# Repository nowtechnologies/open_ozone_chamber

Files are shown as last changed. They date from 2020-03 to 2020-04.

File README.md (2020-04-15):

# SMOG-SC / O3 Sterilizer

*Scalable Modular Ozone Generation based Sterilization Chamber ( SMOG-SC )*

This project aims to lay down general design instructions for an ozone generation based sterilization chamber that could be deployed fast to medical environments. The design is layered and modular to take component availability into account.

## About ozone

Ozone (O3) is an unstable gas comprising three atoms of oxygen. It is unstable because the gas will readily degrade back to its stable state, diatomic oxygen (O2) with the formation of free oxygen atoms or free radicals. The free oxygen atoms or radicals are highly reactive and they will oxidize almost anything  including viruses, bacteria, organic and inorganic compounds) in contacts, making ozone an enormously powerful disinfectant and oxidizer. 

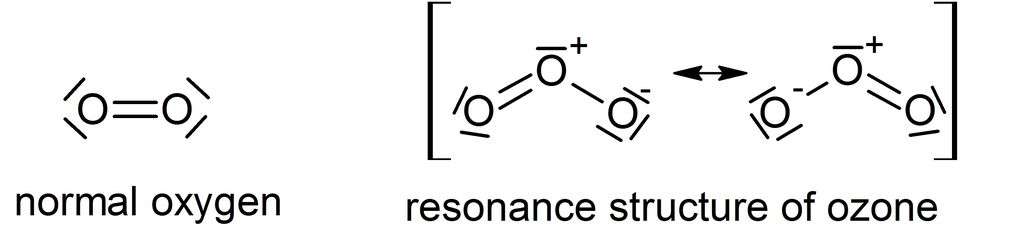
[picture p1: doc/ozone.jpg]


:warning: **Ozone with concentration higher than 1 ppm has adverse effects on human health and the use of ozone for air disinfection is generally not recommended if people are around.** :warning:

The MAC-value is the Maximum Acceptable Concentration a human is allowed to be exposed to for a certain time and certain agent. For ozone the MAC-values is **0.06 PPM for 8 hours a day, 5 days a week** (PPM = Parts Per Million). For a maximum of 15 minutes a MAC-value of 0.3 PPM is applied.

Read more: https://www.lenntech.com/library/ozone/decomposition/ozone-decomposition.htm

| **Temp (°C)** | Half live   |
| ------------- | ----------- |
| -50           | 3 months    |
| -35           | 18 days     |
| -25           | 8 days      |
| 20            | 3 days      |
| 120           | 1,5 hours   |
| 250           | 1,5 seconds |

**Dissolved in water (pH 7)**

| **Temp (°C)** | **Half** **live** |
| ------------- | ----------------- |
| 15            | 30 min            |
| 20            | 20 min            |
| 25            | 15 min            |
| 30            | 12 min            |
| 35            | 8 min             |

* Ozone breaks down to oxygen with a half life of about 20 minutes ( at 20 degrees Celsius in water )
* Decomposition of 2 mol (96 g) ozone to 3 mols of oxygen requires 286 kJ energy
* pH influences acid/base equilibriums of some compounds and also the reaction speed of ozone.
* Decay of ozone in a basic environment is much faster than in an acid environment!
* [Materials ozone resistance chart](https://www.oxidationtech.com/blog/materials-ozone-resistance-chart/)
* [Ozone decomposition kinetics](doc/Ozone_decomposition_kinetics.pdf)

## Decontamination protocol

The standard program adopted involves increasing the ozone level over a period of 15 min to 25 ppm, maintaining this level for 10 min, at which point the humidifier was activated to produce a rapid burst of water vapor. This should result in the RH increasing to > 95% within 5 min. Following this the humidifier and generator are switched off and the catalytic converter is switched on, which results in decrease in ozone to < 1 ppm within 15 min. [Hudson et al.](doc/Ozone_Science_and_Engineering_Pub_Jan091.pdf)

## Device requirements

* Hermetically sealed sterilization chamber *( when door is closed )*
* Effective minimum concentration of ozone is 25 ppm **~50 mg/m3** *( 1 ppm (O3) = 2.14 mg/m3 )*
* To meet protocol parameters **for every cubic meter** a generator capacity of **~200 mg/h** is required.
* Air humidity shall be controlled so that RH could be increased to **> 95%** rapidly. *( optional )*
* There should be a **timed lock**, to prevent the user to open the device while operating. *( optional )*
* There should be a clear **sign** indicating potentially dangerous oxidant levels inside the device.
* Ozone **levels** should be either measured or predicted by its decomposition model.
* Temperature and humidity can be easily monitored. *( supporting the level prediction - optional )*

## System block diagram

:warning: **Note**: our open design is only recommended in emergency situations, where sufficient ventilation of the room can be provided!

The system can be either completely closed or partially open, where the ionized air can travel through the chamber into a catalyst. For the sake of simplicity we chose the closed system design with the <u>generator and the decomposer inside the sterilization chamber</u>.

Either way the sterilizer system consists of four separate modules that can be <u>bought or built</u>:

* The **generator** is turning atmospheric oxygen into ozone enriched air.
* The ozone enriched air is pumped into a sealed **chamber**. 
* The **decomposer** that helps to break down ozone to oxygen.
* The **controller** is regulating the sterilization process.

#### Open system

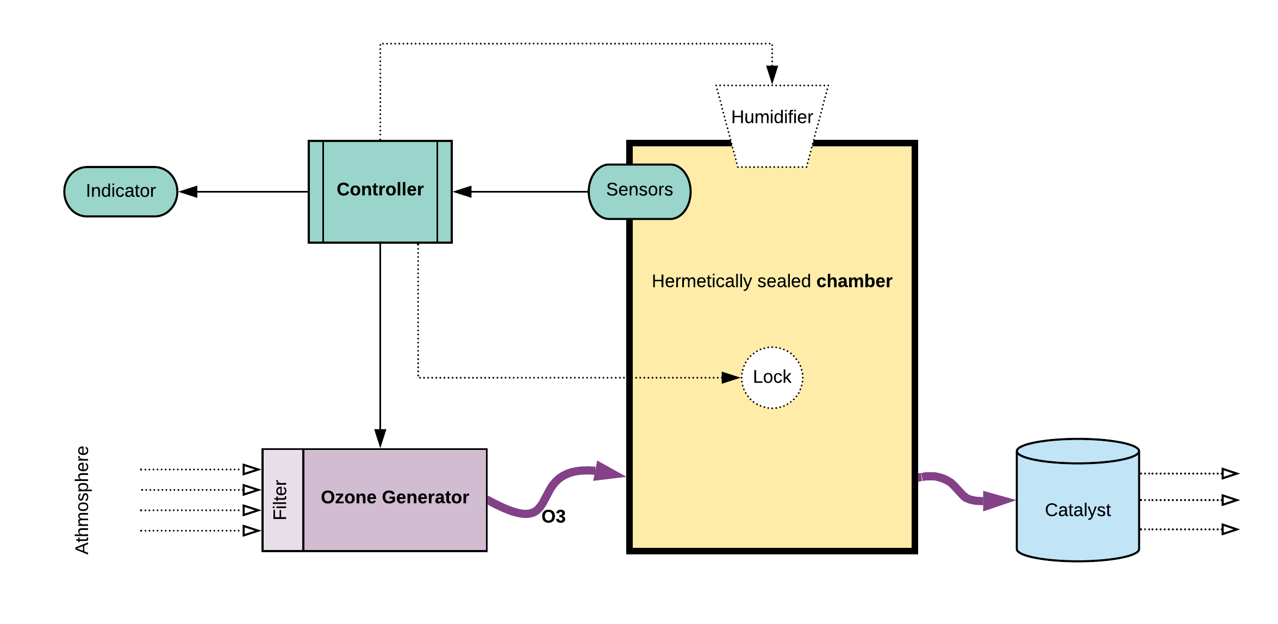
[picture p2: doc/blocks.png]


#### Closed system

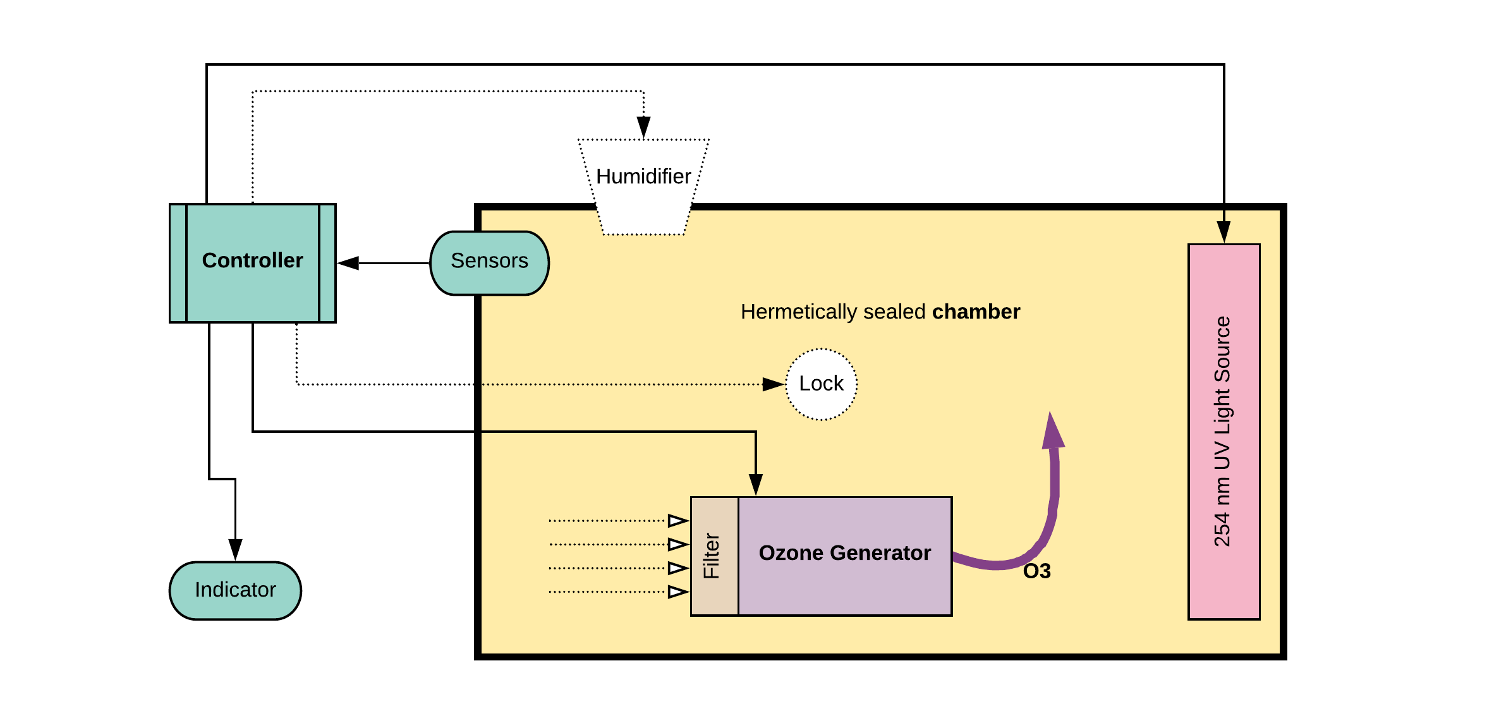
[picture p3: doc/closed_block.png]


### [Ozone generator](doc/ozone_generator.md)

A coronal discharge method based generator consists of:

* HEPA filter on the atmospheric air intake port *( optional )*
* A fan or blower that moves the air volume along the electrodes. *( AC or low voltage DC )*
* The electrodes or *"ozone plates"* provide surface for the corona discharge. *( ceramic )*
* A high voltage power supply ( output **~3.5kV / 30mA** ) is required to drive the plates.
* Exhaust port to channel the O3 enriched air into an ozone resistant tube.

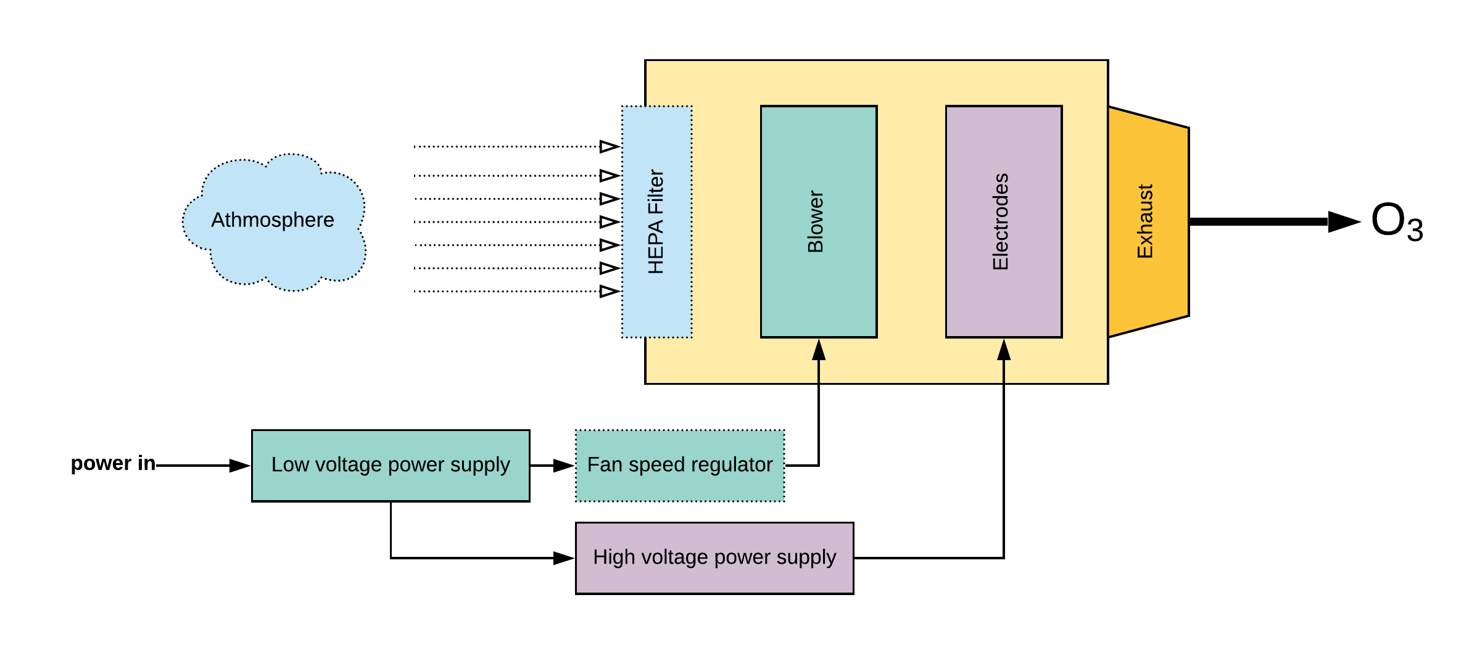
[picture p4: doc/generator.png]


For ultraviolet radiation based ozone production: *( this method is less efficient )*

* Powerful light emitter with a spectral peak of 185 nm.
* A fan or blower that moves the air.

### [Sterilization chamber](doc/steril_chamber.md)

* The chamber has to be somewhat airtight as the ozone is harmful to humans as well.
* Ozone, temperature and humidity sensors has to be placed inside.
* Ideally an electric lock should block the door.

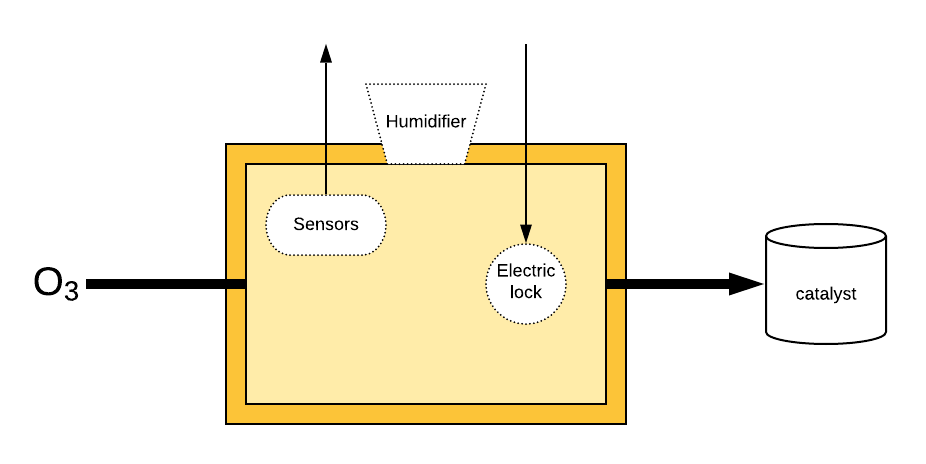
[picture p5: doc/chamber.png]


### [Decomposer](doc/decomposer.md)

Ozone can be reduced to oxygen **thermally** or **catalytically** or **by radiation**. 

*In case of a closed system:*

* The chamber has to hold light sources at **254 nm** wavelength with sufficient power to disrupt the instable bonds in ozone molecules.

*In case of an open system:*

* The ozone enriched air from the chamber has to be able to enter the decomposer.
* In case of catalytic destruction the decomposer could be a bucket of tap water.
* If the pH can be controlled, basic environment is preferable. *( Pka  = 10,3 )*
* Thermal decomposition is effective if the air flows through a tube heated to **250 C** *( HL = 1.5s )*

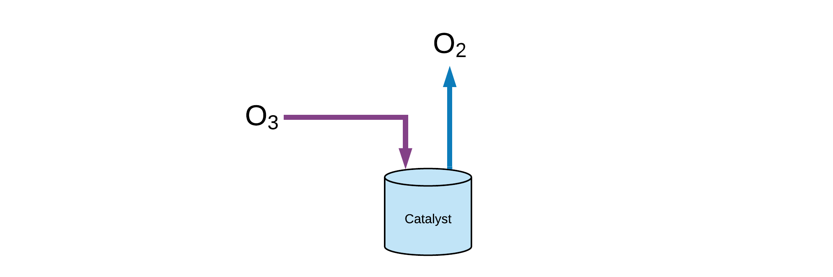
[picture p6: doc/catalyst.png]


### [Process controller](doc/ots_controller.md)

*  There are ready made [ozone controllers](http://www.iaq.hu/F2077TSM-O3%20ozontavado.pdf) with relayed outputs.

**Otherwise a controller could consist of:**

*  MCU chip or board *( general programmable micro controller board e.g. Nucleo or Arduino )*
* Temperature sensor to support the decomposition model and compensate for ozone readings.
* Humidity sensor to check protocol requirements are met and compensate for ozone readings.
* Ozone sensor as control feedback and to check protocol requirements.
* Optional user interface *( Small OLED display and rotary encoder )* for setting chamber parameters
* Single button to start / stop sterilization process.
* Process indicator *( e.g. large LED )*
* Interfaces to control the ozone generator, humidifier and lock. *( e.g. solid state relays )*

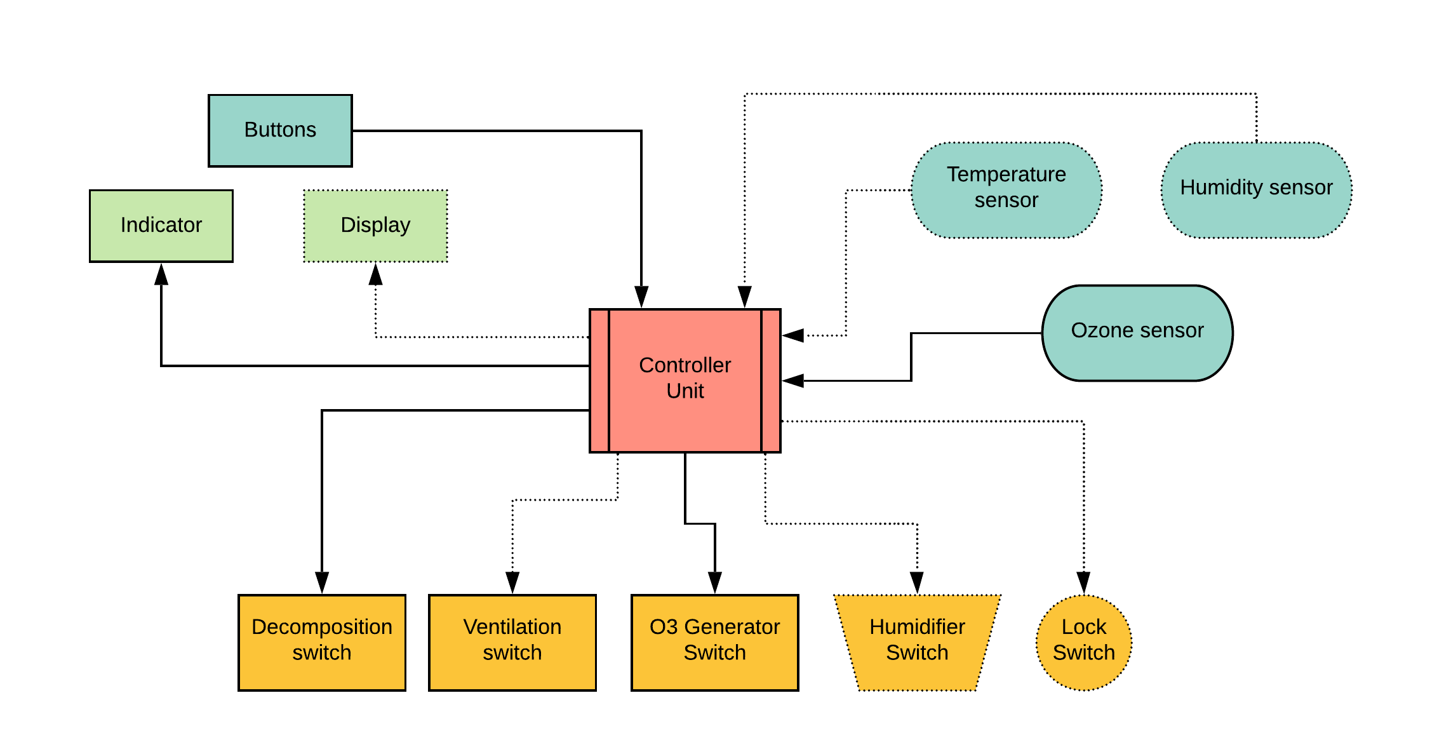
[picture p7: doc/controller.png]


## Build instructions

### Closed system assembly

1. [Modify a refrigerator](doc/refrigerator.md)
2. [Buy an off the shelf generator module](doc/ozone_generator.md)
3. [Buy an off the shelf ozone controller](doc/ots_controller.md)

### How to build an Ozone Generator

* If an off-the-shelf generator is not available:
  * Here is how to [build it from modules](doc/ozone_generator.md). 
  * And if you can't find modules anymore here is how to [build it from components](doc/ozone_generator.md).
* Find information on [how to create the electrodes](doc/electrodes.md) itself.
* Generator [capacity measurement instructions](doc/capacity.md).

### How to build and Ozone Sensor

[Open ozone sensor](https://github.com/nowtechnologies/open_ozone_sensor)

### How to build and Ozone Monitor

[Open ozone monitor](https://github.com/nowtechnologies/open_ozone_monitor)

### How to build an Ozone Controller

[Open ozone controller](https://github.com/nowtechnologies/open_ozone_controller)

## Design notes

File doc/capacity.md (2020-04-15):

# Determining generator capacity

For detailed description of different methodologies please read the article of *Kerwin Rakness* on **Guideline for Measurement of Ozone Concentration in the Process Gas From an Ozone Generator** [here](Ozone_measurement.pdf).

Follow [Oxidation Technologies Measurement protocol](https://www.oxidationtech.com/ozone/ozone-production/how-to-test-production-from-your-ozone-generator/test-o3-output-commercial.html):

An **ozone meter** will be required to measure ozone concentration in the air leaving the ozone generator. This must have a sample pump to draw a sample of gas from your flow tube into the monitoring device. This will provide the most accurate ozone measurements without disrupting your air flow. Ideally a UV based ozone analzyer will be used to measure ozone levels due the greater precision and accuracy available. However, there are some ozone meters available using electrochemical or HMOS sensor cells that can pull a gas sample into the sensor and provide reasonable accuracy. For the best accuracy in ozone production choose the most accurate ozone meter possible.

The specific ozone analyzer we recommend to use for this testing is the [UV-100 Ozone Analyzer.](https://www.oxidationtech.com/products/ozone-monitors/uv-analyzer/uv100-ozone-analyzer.html) This is available[ for sale](https://www.oxidationtech.com/products/ozone-monitors/uv-analyzer/uv100-ozone-analyzer.html), or [for rent for shorter term needs.](https://www.oxidationtech.com/products/rent-ozone/uv-100-rental.html)

A **Monometer** is used to measure airflow by measuring the velocity of airflow in your flow tube. A digital monometer can be obtained that will measure airflow in a variety of units of measure. For the best accuracy in ozone production choose the most accurate monometer possible.

A **Flow Tube** must be constructed to measure airflow from the ozone generator. This tube can be constructed of PVC or other plastic materials. The airflow from the ozone generator must have as much turbulence removed as possible to accurately measure air speed. This tube must be sealed directly to the outlet of the ozone generator and must not restrict air flow in any way. Actual air flow of the ozone generator in normal operation must be obtained and measured accurately.

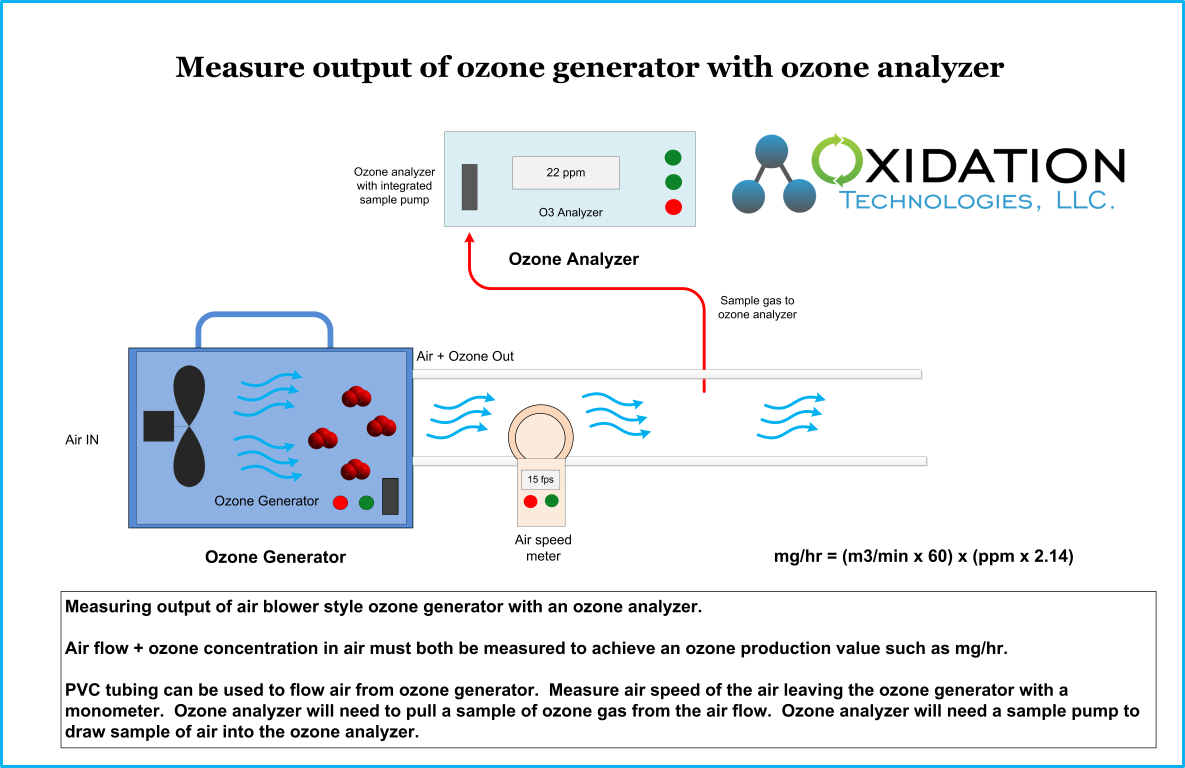
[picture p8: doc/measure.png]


## Ozone meters

Simplest way to determine the capacity of a generator is with a calibrated measurement unit, such as this:

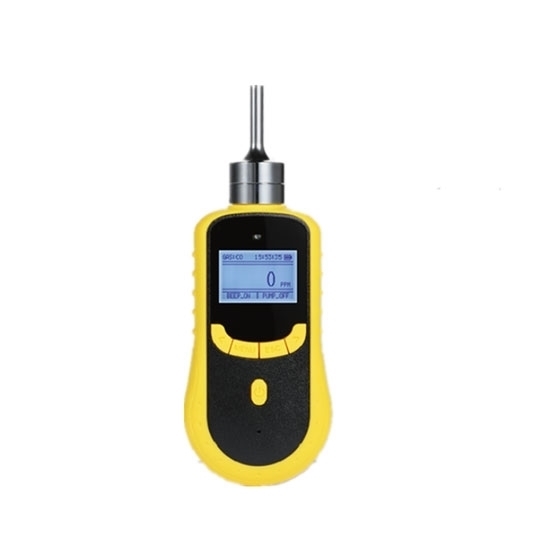
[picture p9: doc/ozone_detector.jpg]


* Typical range 10 ppm - 1000 ppm
* Price 250 - 1500 EUR

## Open ozone sensor + PC GUI

#### [OO/Sensor](https://github.com/nowtechnologies/open_ozone_sensor)

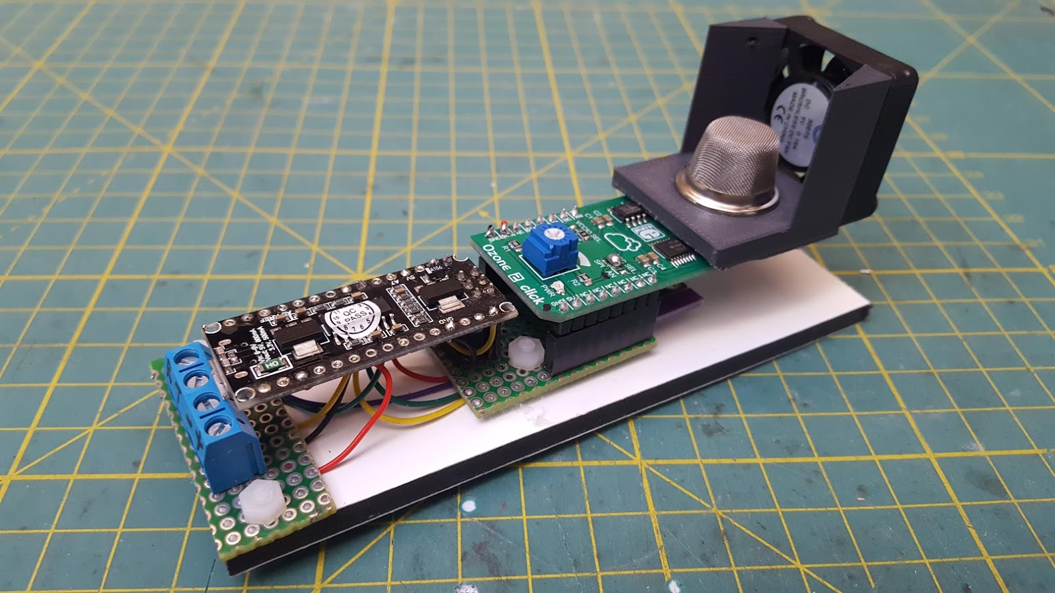
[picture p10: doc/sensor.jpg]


* Typical range 10 ppm - 1000 ppm
* Price <50 EUR

#### [OO/Monitor](https://github.com/nowtechnologies/open_ozone_monitor)

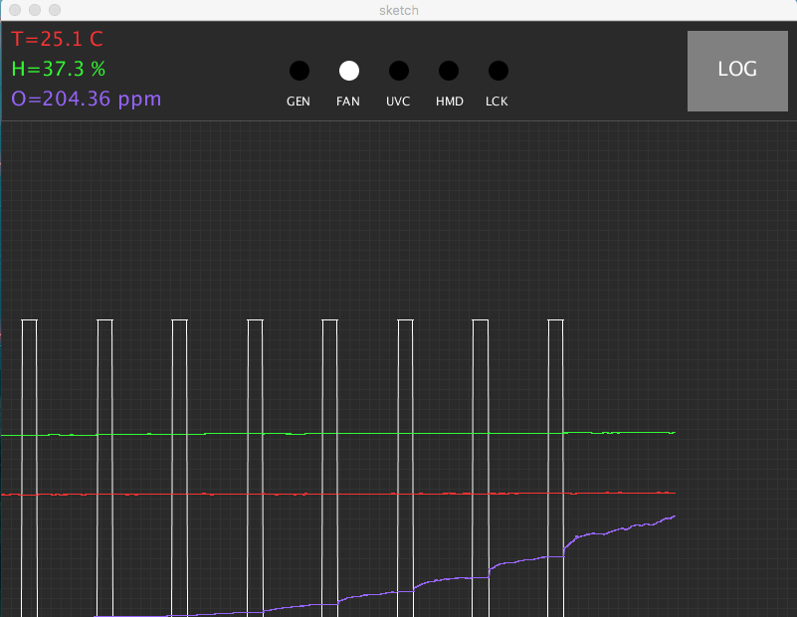
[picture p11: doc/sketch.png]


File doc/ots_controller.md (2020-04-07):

# Process controller

## Ozone controllers

https://www.ecosensors.com/product/os-6-ozone-controller-data-sheet/

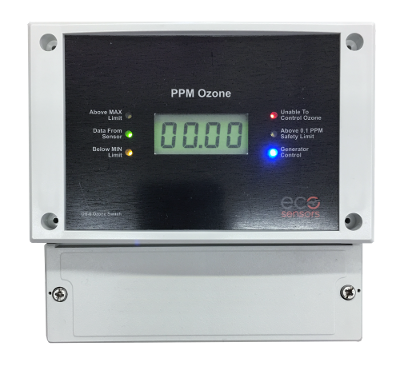
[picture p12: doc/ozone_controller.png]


The OS-6 is an industrial grade ozone controller and monitor. The OS-6 design has been optimized for accuracy, ease of installation, setup and operation. The OS-6 is only available with the SM-7/SM-EC in two different concentration ranges.

**Features:**

- Industrial strength, water resistant enclosure.
- Large digital display, auto-ranging (0-50ppm) w/ backlight.
- Easy front panel access to set points and relays.
- Precisely adjustable max, min, and fail time set points.
- Failure alarm if ozone remains outside control range.
- Front panel generator control cutoff switch for easy maintenance.
- User selectable PPM ranges for analog output (4-20 mA and 0-2 VDC)
- OSHA 0.1 ppm safety limit light.

## Open Ozone Controller

[Github project](https://https://github.com/nowtechnologies/open_ozone_controller)

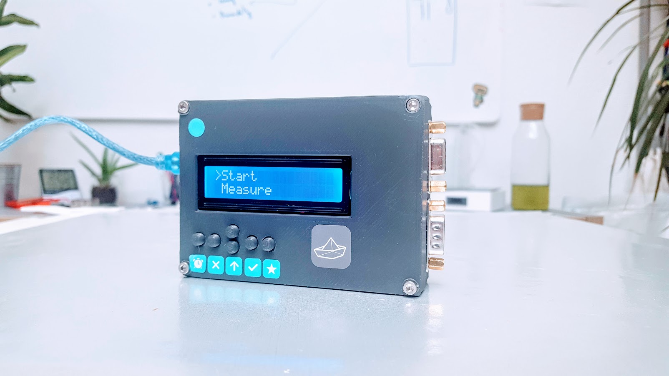
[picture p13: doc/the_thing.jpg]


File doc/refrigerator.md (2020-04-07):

# D.I.Y. sterilization chamber 

*How to modify a refrigerator*

## Tools

* Side cutter
* Screw driver
* Knife
* Duct tape

## Preparing the refrigerator 

Refrigerators seal very good in general hence they are good candidates as a sterilization chamber. They are fairly easy to acquire as every household has one, but it can be utilized **only after a careful preparation** as in many cases it contains **flammable gas!** 

:warning:**Please follow [this link](https://www.kth.se/en/2.2145/energiteknik/forskningsavdelningar/ett/projekt/koldmedier-med-lag-gwp/low-gwp-news/nagot-om-koldmediers-brannbarhet-1.575938) to learn more about the refrigerant in your device before proceeding.** :warning:

### Remove the electric plug

Find the distributor box ( probably near the compressor ), pull the cables out so that you can see their color codes ( if possible ) then cut them one by one. Don't throw out the cable with the wall plug, we are going to reuse it.

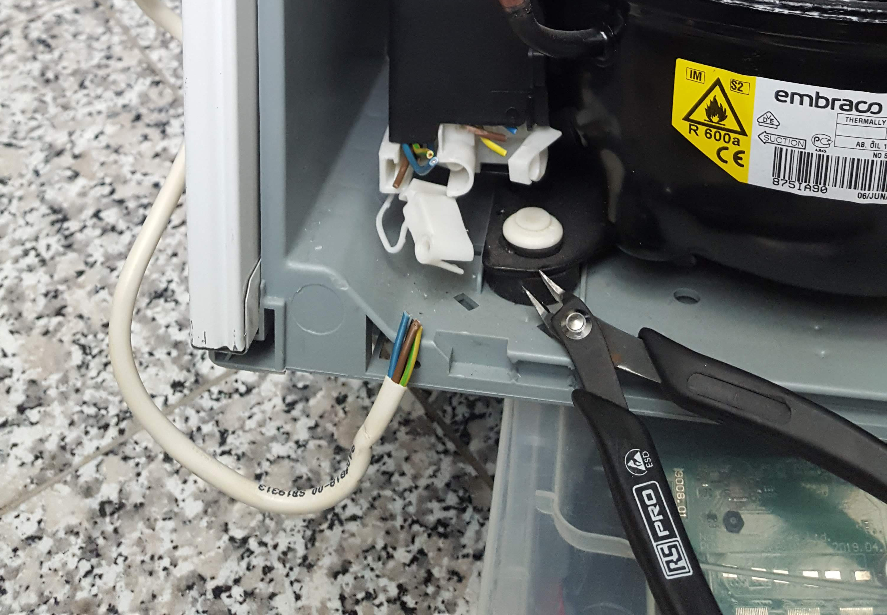
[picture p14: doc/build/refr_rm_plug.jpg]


### Degassing :warning:

This step is **dangerous** as most refrigerators in Europe are filled with **R600** gas that is highly flammable. The system has to be degassed very slowly to avoid risk. Take the refrigerator outside to **open air** before continuing with this step! **Avoid any probability and proximity to open flame or sparks at all times during the degassing process.**

1. Find a cartridge shaped gas puffer that has - usually - a thinner copper tube coiled around it.
2. **Cut the thin copper tube and step aside until you don't hear it hiss anymore.** *( marked as 1st )*
3. Now cut the thicker copper tube connected to the cartridge *( marked as 2nd )*
4. After this you can cut any other copper tubing wherever you want.

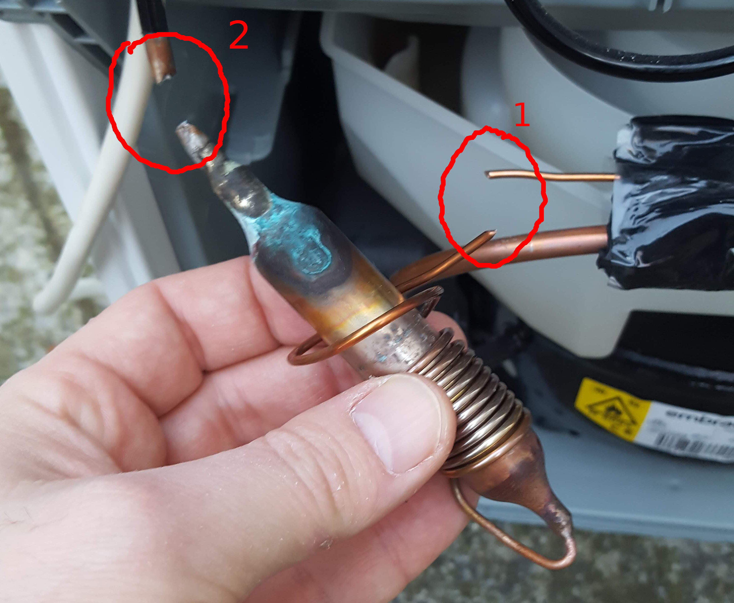
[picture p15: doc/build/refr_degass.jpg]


### Remove the cooler plate

Cut the remaining tubing that connects the cooler plate. Remove the screws or patents that hold the cooler on it's place and get rid of the plate.

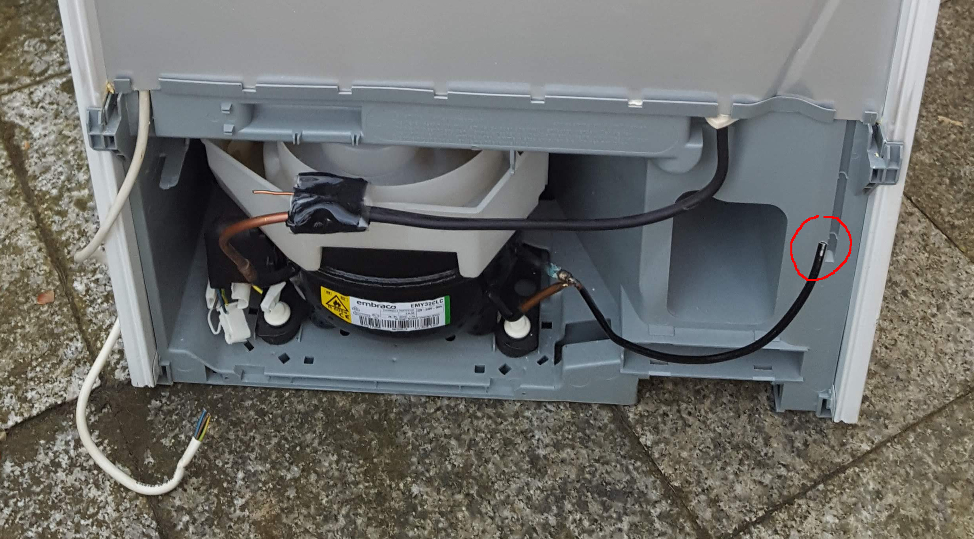
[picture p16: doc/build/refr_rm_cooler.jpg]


### Remove the compressor

Now that the cooler plate gone, cut the last copper tube that connects the compressor. Remove screws or patents holding it in it's place, then remove the compressor.

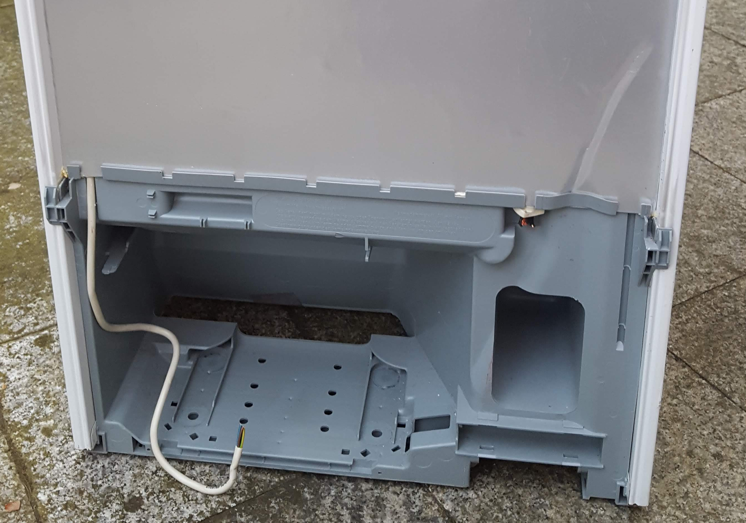
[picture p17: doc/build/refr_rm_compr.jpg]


### Seal the sinker hole

Every refrigerator has a hole to allow the damp to drip down. **This has to be sealed!** Use silicone or duct tape to seal it.

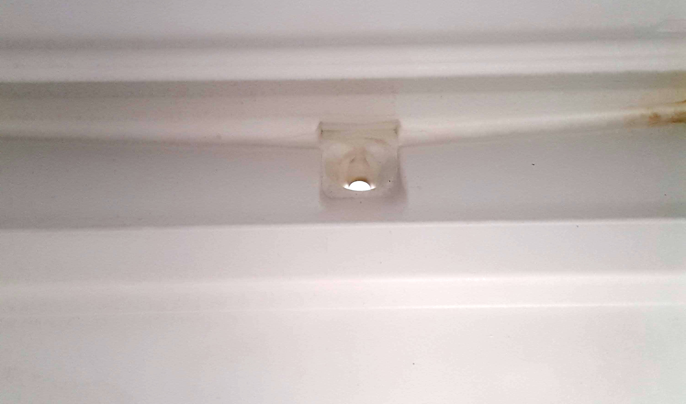
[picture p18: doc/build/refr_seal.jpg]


### Remove the switch and light

There is usually a switch and a light bulb inside the icebox that leaves us an opportunity to use it's wiring to power the ozone generator without drilling a hole into the fridge. *( The switch could be used to disable the generator when the door has been opened, so don't throw it away. )* Remove the whole pack.

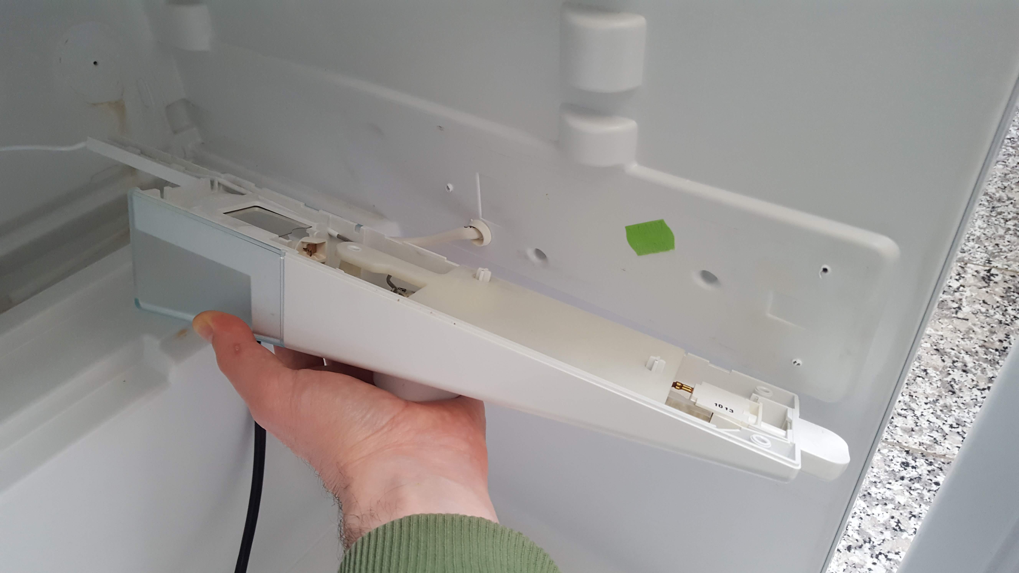
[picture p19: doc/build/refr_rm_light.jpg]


## Rewiring

### Prepare the wall plug

Use screw terminal block to connect the three wires of the wall plug cable to the three wires of the light cable, maintain color coding. The ozone generator requires a properly grounded connection.

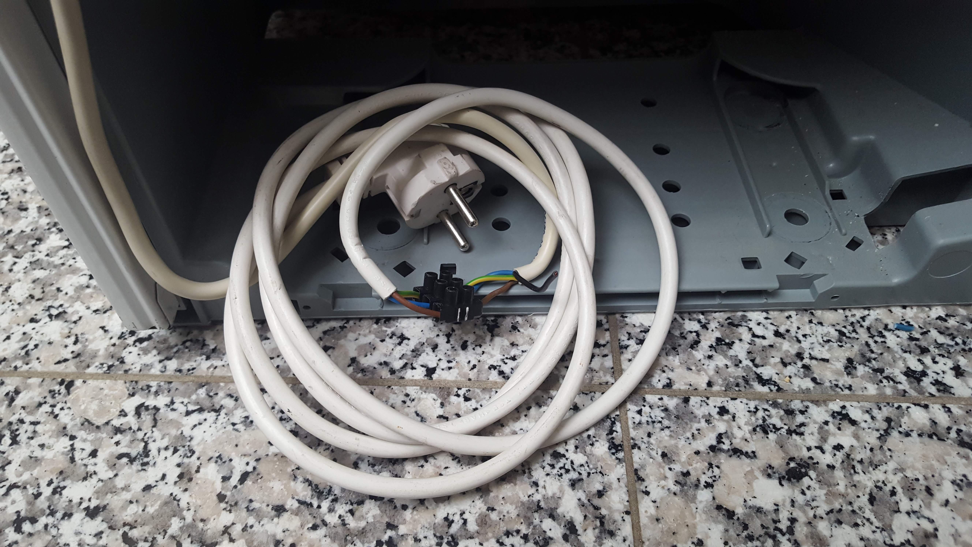
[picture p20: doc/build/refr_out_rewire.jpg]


### Add internal terminals

Now add screw terminals to the internal end of the same cable. *( Note: there is sometimes an extra black wire for the switch, just ignore it for now. )*

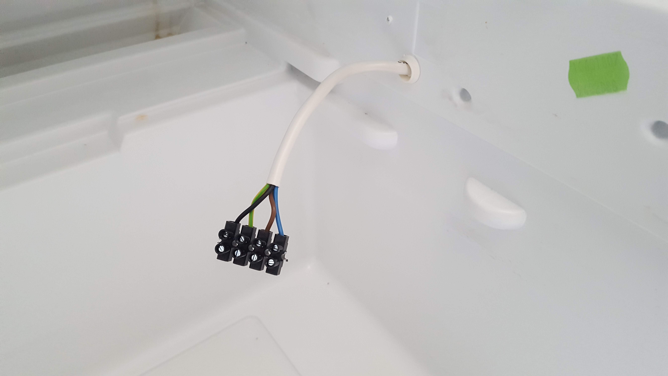
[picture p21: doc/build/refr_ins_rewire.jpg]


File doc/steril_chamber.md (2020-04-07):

# Sterilization chamber



## Off the shelf cabinets

**Requirements:**

* Preferably stainless steel
* Hermetically seal-able

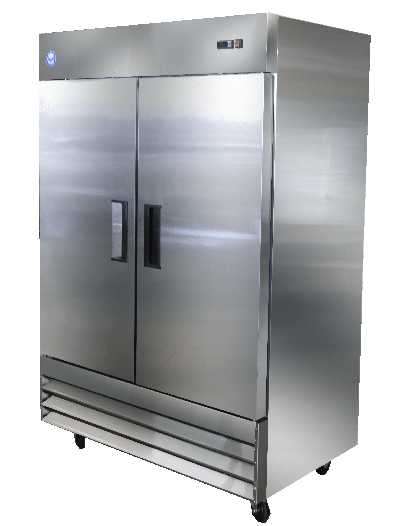
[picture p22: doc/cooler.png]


## Refrigerators

Refrigerators seal very good in general hence they are good candidates as a sterilization chamber. They are fairly easy to acquire as every household has one, but it can be utilized **only after a careful preparation** as in many cases it contains **flammable gas!** 

[Here is how to modify one.](refrigerator.md)

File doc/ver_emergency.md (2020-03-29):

# How to build a sterilizer blazing fast

:warning: These instructions are for emergency situations, where all off-the-shelf components are at hand and there is very short time to produce a working sterilizer. In any other case please build one that has an ozone detector based process controller.

### :construction: WARNING: Disinfection protocols are not finalized yet! :construction:

## Components

* Refrigerator
* Ozone generator
* Timer switch
* Screw terminal block

## Tools

* Side cutter
* Screw driver
* Knife
* Duct tape

## Preparing the refrigerator 

Refrigerators seal very good in general hence they are good candidates as a sterilization chamber. They are fairly easy to acquire as every household has one, but it can be utilized **only after a careful preparation** as in many cases it contains **flammable gas!** 

:warning:**Please follow [this link](https://www.kth.se/en/2.2145/energiteknik/forskningsavdelningar/ett/projekt/koldmedier-med-lag-gwp/low-gwp-news/nagot-om-koldmediers-brannbarhet-1.575938) to learn more about the refrigerant in your device before proceeding.** :warning:

### Remove the electric plug

Find the distributor box ( probably near the compressor ), pull the cables out so that you can see their color codes ( if possible ) then cut them one by one. Don't throw out the cable with the wall plug, we are going to reuse it.



### Degassing :warning:

This step is **dangerous** as most refrigerators in Europe are filled with **R600** gas that is highly flammable. The system has to be degassed very slowly to avoid risk. Take the refrigerator outside to **open air** before continuing with this step! **Avoid any probability and proximity to open flame or sparks at all times during the degassing process.**

1. Find a cartridge shaped gas puffer that has - usually - a thinner copper tube coiled around it.
2. **Cut the thin copper tube and step aside until you don't hear it hiss anymore.** *( marked as 1st )*
3. Now cut the thicker copper tube connected to the cartridge *( marked as 2nd )*
4. After this you can cut any other copper tubing wherever you want.



### Remove the cooler plate

Cut the remaining tubing that connects the cooler plate. Remove the screws or patents that hold the cooler on it's place and get rid of the plate.



### Remove the compressor

Now that the cooler plate gone, cut the last copper tube that connects the compressor. Remove screws or patents holding it in it's place, then remove the compressor.



### Remove the switch and light

There is usually a switch and a light bulb inside the icebox that leaves us an opportunity to use it's wiring to power the ozone generator without drilling a hole into the fridge. *( The switch could be used to disable the generator when the door has been opened, so don't throw it away. )* Remove the whole pack.



## Rewiring

### Prepare the wall plug

Use screw terminal block to connect the three wires of the wall plug cable to the three wires of the light cable, maintain color coding. The ozone generator requires a properly grounded connection.



### Add internal terminals

Now add screw terminals to the internal end of the same cable. *( Note: there is sometimes an extra black wire for the switch, just ignore it for now. )*



### Prepare generator cable

Now repeat the step with the cable provided for the generator, and connect it to the terminals inside the fridge. Make sure it's long enough to place the generator anywhere you planned.

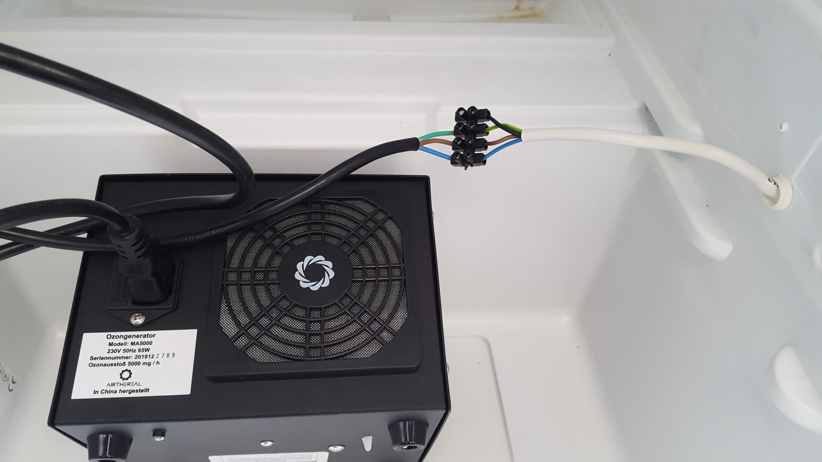
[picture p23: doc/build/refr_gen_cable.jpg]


### Install the generator

Place the generator so that neither the intake for it's fan nor the exhaust panel is blocked. 

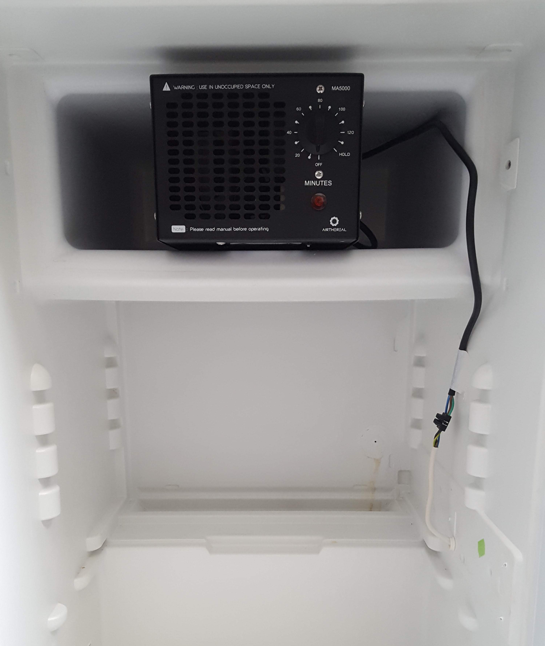
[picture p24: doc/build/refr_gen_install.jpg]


### Seal the sinker hole

Every refrigerator has a hole to allow the damp to drip down. **This has to be sealed!** Use silicone or duct tape to seal it.



## Using the emergency sterilizer

:warning: Please use this device only if you are sure that you can vent the room frequently, as without precise controller there is going to be excess ozone gas in the container on the end of each sterilization cycle. Follow procedure and do not exceed MAC exposure. **MAC = 0.06 PPM for 8 hours a day, 5 days a week.**

### Enable continuous generator operation

Most generators' - that have analogue timer built in - continuous operation can be enabled, by selecting the "hold" function on their dial. If you are using a more precise timer, or an ozone controller you should enable this function on the generator. ( If there is no such dial, then the device is probably already in continuous operation mode. If there is no "hold" function on the dial, the device has to be disassembled and the timer switch has to be shorted. )

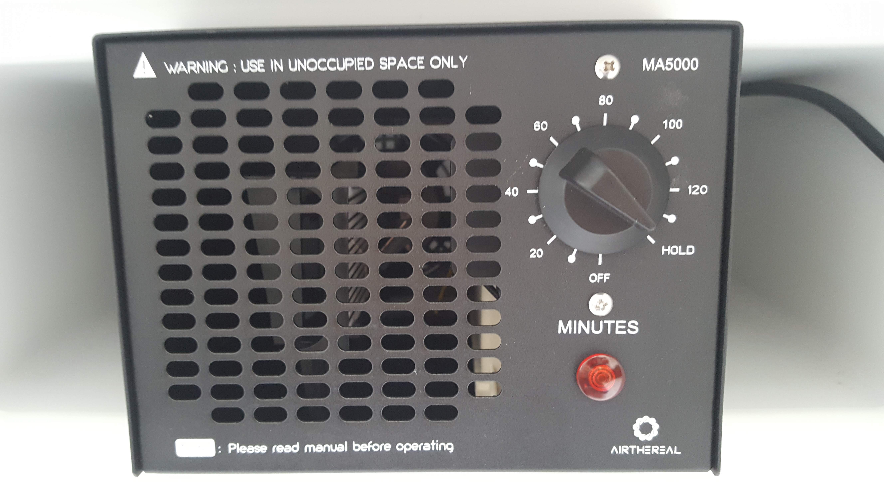
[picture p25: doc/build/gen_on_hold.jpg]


### Preparations

:warning: **Use our [volume to treatment time converter tool](http://nowtech.cloud/closed_calc.html) to figure out the timing protocol.** For smaller containers and large generators meant for room sized air purification the treatment times are going to be under a minute.

:warning: Most timer switches embedded into the generators are not able to do sub-minute timing. **You have to connect the system through a digital or analogue timer switch that is able to do the precise time switching.**

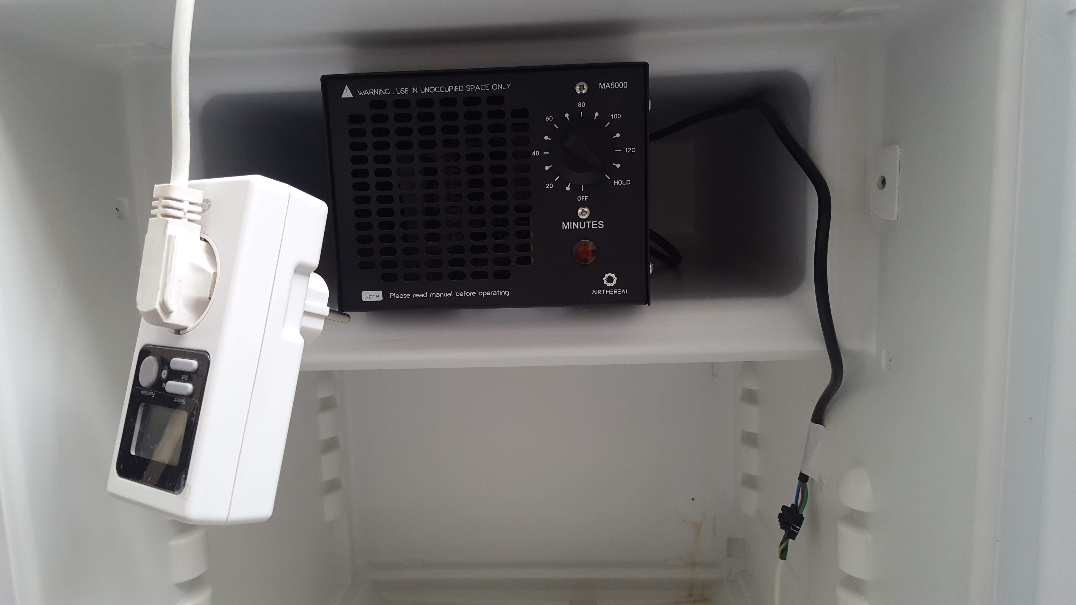
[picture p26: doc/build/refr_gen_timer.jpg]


# :construction:

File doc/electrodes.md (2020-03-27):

# Electrode alternatives

## Glass tube

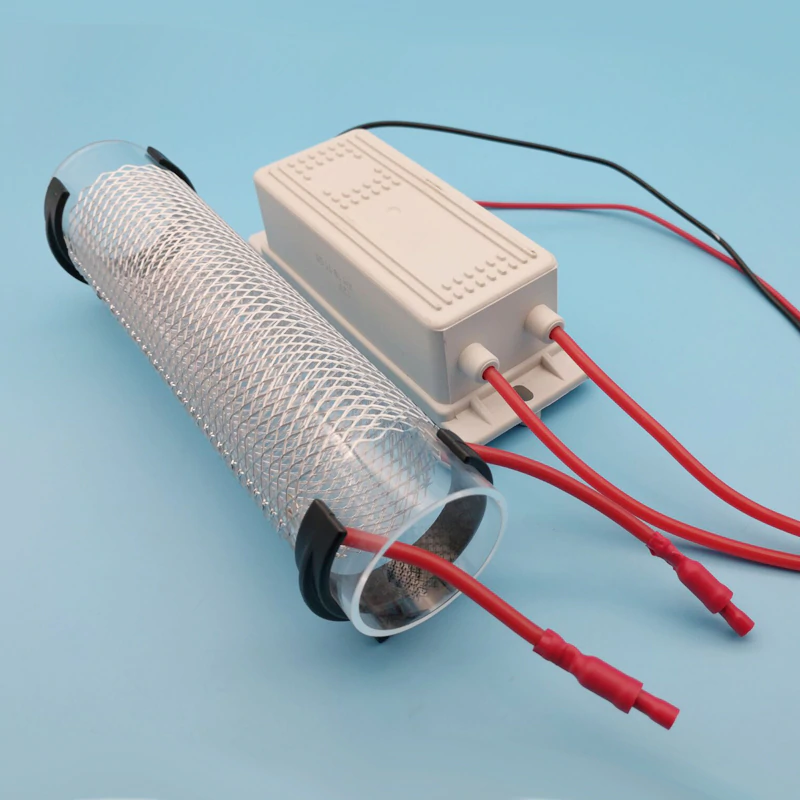
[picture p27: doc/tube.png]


## Stainless steel saw

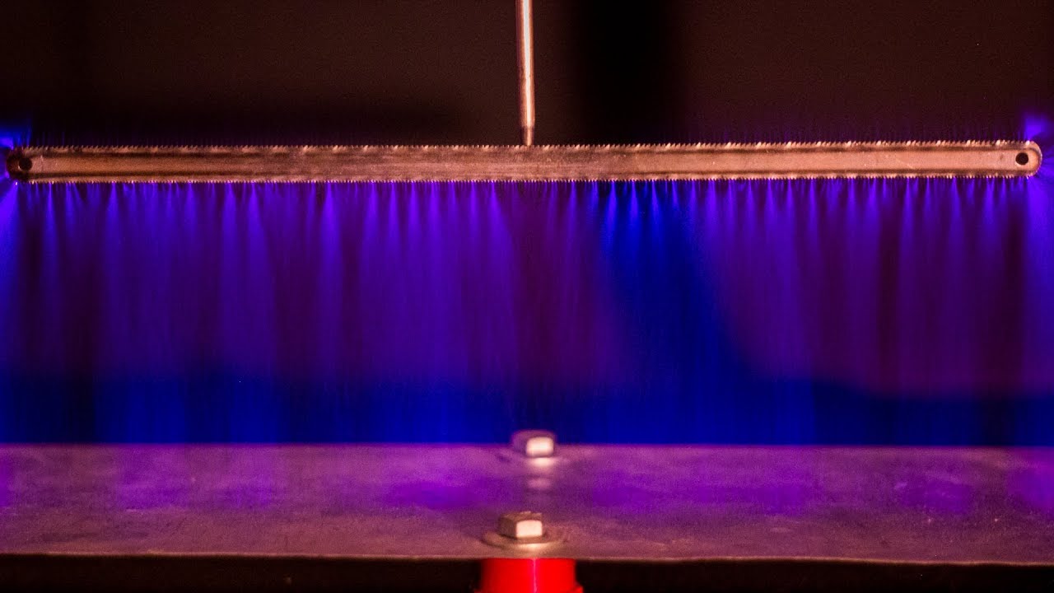
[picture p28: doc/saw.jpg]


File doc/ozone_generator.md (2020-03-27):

# Ozone generator



## Off the shelf generators

Room and car air purifiers can meet the requirements if we take into consideration that **for every cubic meter** a generator capacity of **~200 mg/h** is required. Mid-sized generators for homes produce between 2.5 - 10 grams / hour.

#### Advantages

* Fastest way to start with. *( Put it in a closed chamber and turn it on for n minutes. )*
* It has been built and tested.
* It has the capacity to sterilize a complete room. *( 5-10 g/h )*
* The indicator and timer is already built in. *( also potential disadvantage )* 

#### Disadvantages

* Price range can vary from 100-1000 EUR.
* It runs only from AC. *( battery operation requires disassembly or an inverter )*
* There might be some difficulties with the supply chain.

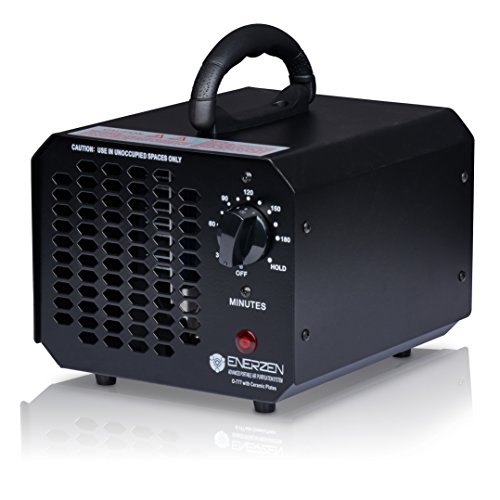
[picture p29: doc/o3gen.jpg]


## Ozone generator modules

Generator modules come in different shapes and sizes, the most frequent types are based on ceramic plate electrodes. These modules also easily met the minimum capacity requirements. As a thumb rule one plate *( ~100x50mm )* can produce ~5 g/h ozone. The modules can be either DC or AC powered by type.

#### Advantages

* Fairly fast way to start with.
* Functional module, already tested.
* More then enough capacity.
* Easy to scale up.
* Easy to control.
* Fair price *( as of know ~30 EUR for a 10 g/h module )*

#### Disadvantages

* All the other components needs to be built around it. 
* There might be some difficulties with the supply chain. *( as produced in China )*

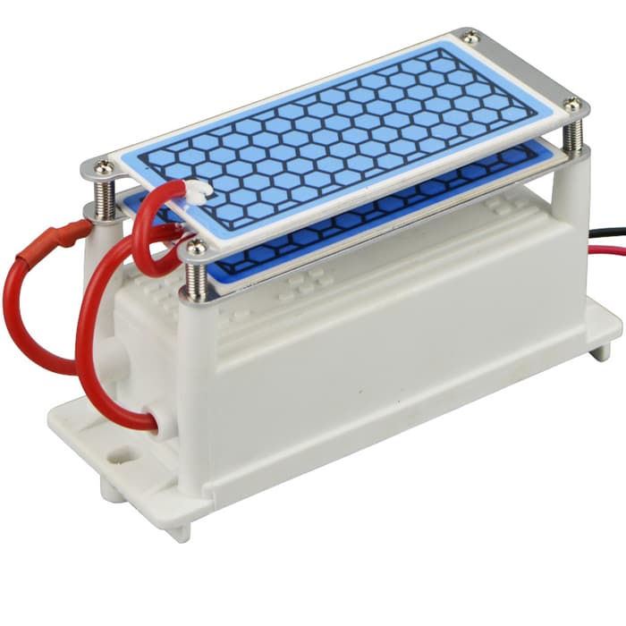
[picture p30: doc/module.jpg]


#### Simple generator configuration

The most easy to assemble setup for a functional generator is to an AC fan ( ~100 CFM = ~170 m3/h ) with an AC generator module:

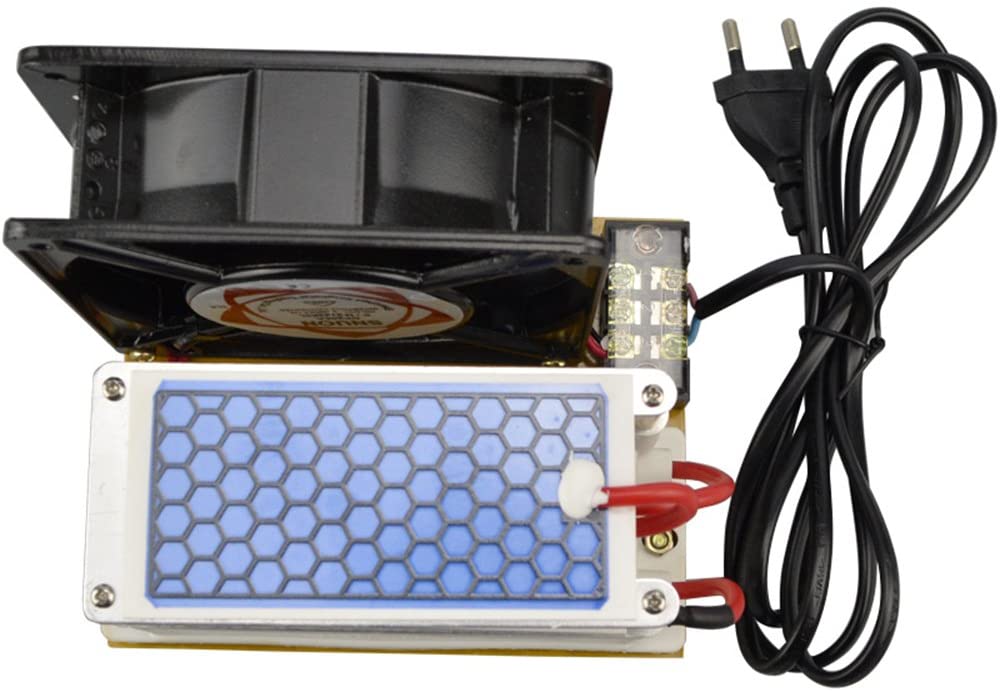
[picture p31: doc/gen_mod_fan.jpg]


## Generator module from scratch

At a pinch the generator can be built from electronic modules and the modules from simple components:

* Ozone plates / electrodes

* High voltage power supply *( HV-PSU )*

### Electrodes

The electrodes are the **critical parts** of a generator as the instable ozone molecules are formed when the atmospheric oxygen molecules are forced into a higher energy state by the corona arc on the surface of the electrodes. Corona is generated by applying high voltage electrical energy to the active element on the electrode and then discharging this energy through the dielectric ceramic to the ground pole. This process generates a significant amount of heat. The more power applied the greater the heat generated.



#### Ready made plates

* https://www.sihon-ozone.com/product-items/ozone-ceramic-plates/

#### [Alternative electrodes](electrodes.md)

* Glass sheet or tube with aluminum wire structures on both sides
* Sheets of stainless steel with saw forming edges *( arc gap on the edges )*
* Double sided printed circuit board  *( Preferably aluminum base layer )* 

### High voltage power supply

:warning: The ceramic plates run on **3.5 kV** alternating current of **30 mA** and **18.5 KHz** :warning: 

Depending on its electronic design the HV-PSU can be either an AC/DC or a DC/DC transformer.

#### Off the shelf neon sign transformer

* Mind the input power - usually ~230 AC, but in case of a switching unit it can be also DC 12V / 24V 
* Output should be between 3 - 5 kV and 20 - 50 mA
* Output frequency should be between 12 - 100 KHz for continuous corona arc
* Connect the output to the ozone plate *( or to the manufactured electrodes )* to create a generator module



#### Power supply designs

Generally speaking there are two stages in a high voltage PSU, a waveform generator and a voltage multiplier. 



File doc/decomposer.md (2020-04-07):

# Ozone destruction methods

## Ultraviolet light





## pH regulated water solutions



## Extreme heat



| **Temp (°C)** | Half life   |
| ------------- | ----------- |
| -50           | 3 months    |
| -35           | 18 days     |
| -25           | 8 days      |
| 20            | 3 days      |
| 120           | 1,5 hours   |
| 250           | 1,5 seconds |

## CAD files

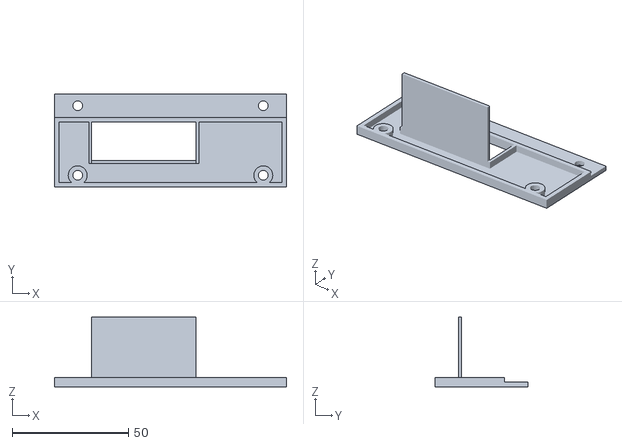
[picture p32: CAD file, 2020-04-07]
models/lock/UAL_rack_cover_LT.stl
100.0 x 40.0 x 30.0

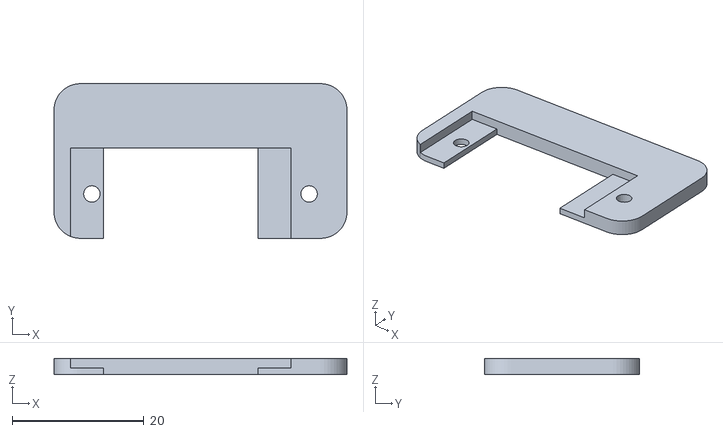
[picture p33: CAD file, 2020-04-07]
models/lock/UAL_servo_holder.stl
44.5 x 23.5 x 2.50

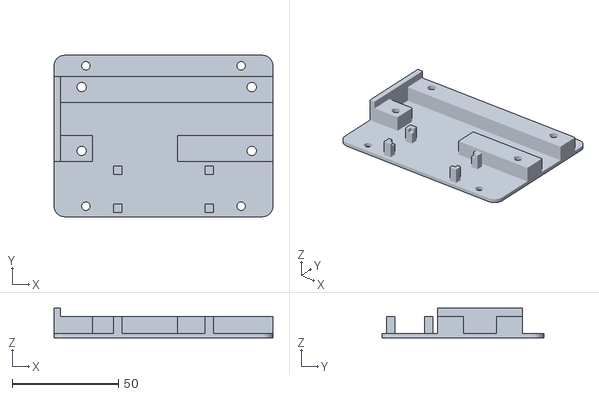
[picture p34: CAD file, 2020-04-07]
models/lock/UAL_baseplate.stl
103.0 x 76.0 x 14.0

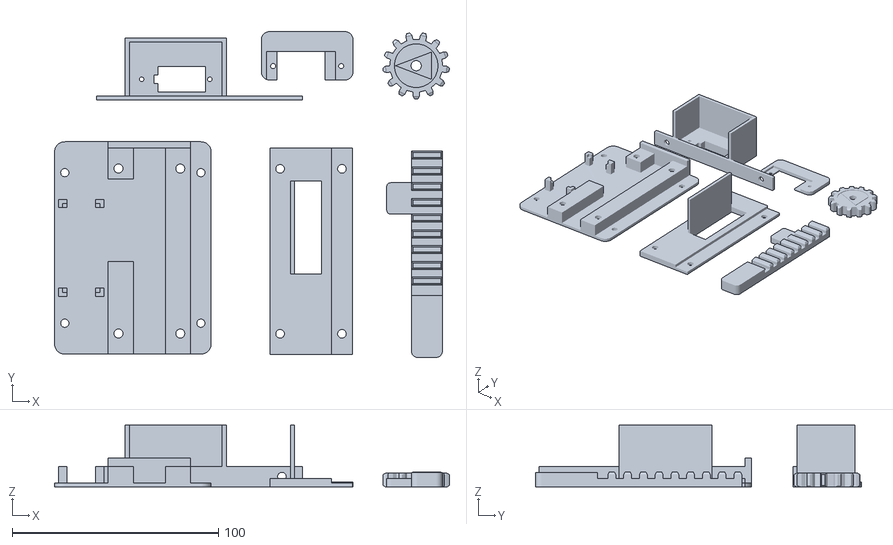
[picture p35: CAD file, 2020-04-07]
models/lock/UAL_all.stl
191.5 x 158.0 x 30.0

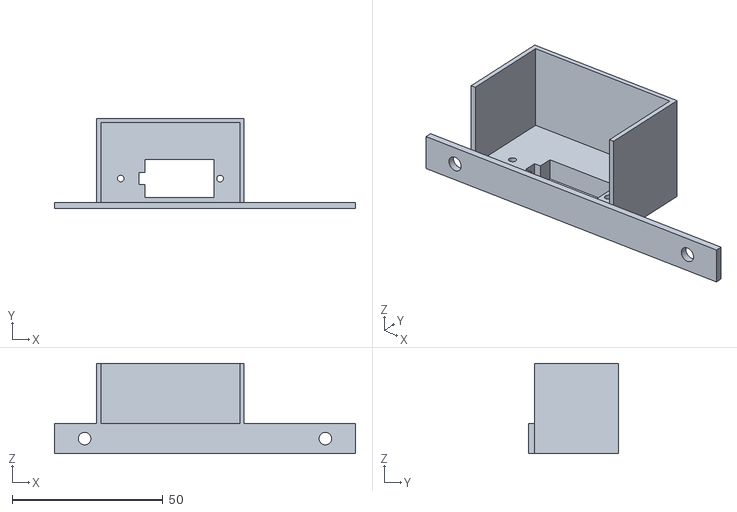
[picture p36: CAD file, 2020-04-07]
models/lock/UAL_servo_cover_LT.stl
100.0 x 30.0 x 30.0

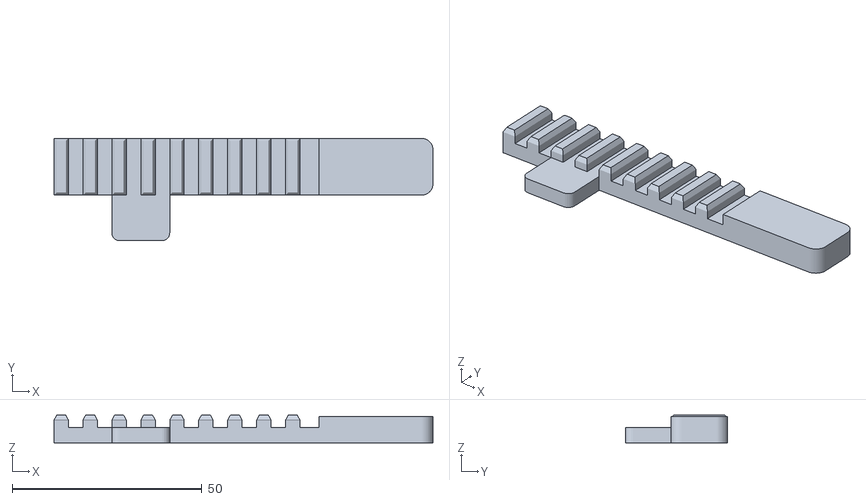
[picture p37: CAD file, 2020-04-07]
models/lock/UAL_rack.stl
100.0 x 27.0 x 7.30

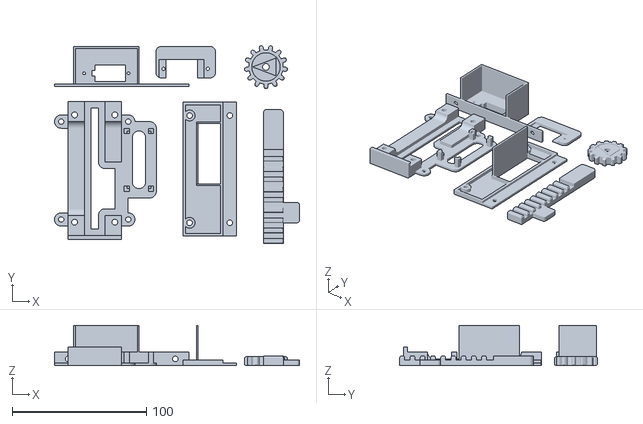
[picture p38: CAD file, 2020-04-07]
models/lock/UAL_all_LT.stl
182.7 x 147.5 x 30.0

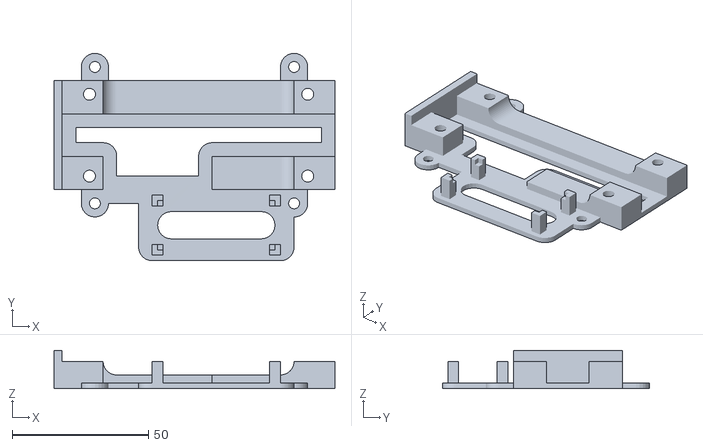
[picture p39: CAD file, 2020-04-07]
models/lock/UAL_baseplate_LT.stl
103.0 x 76.0 x 14.0

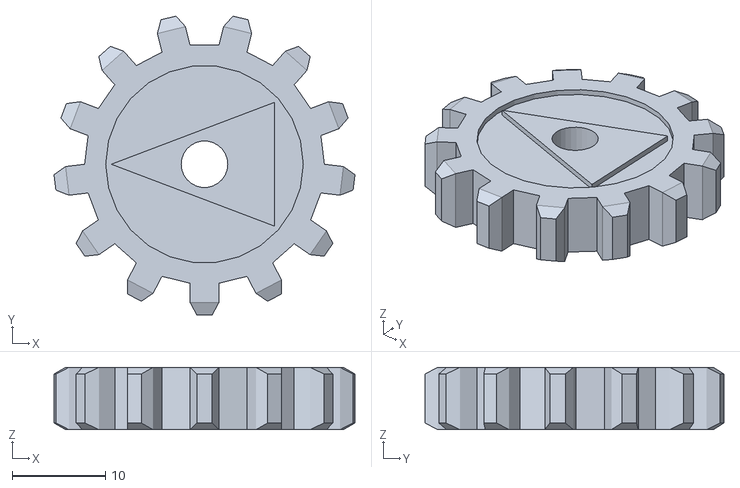
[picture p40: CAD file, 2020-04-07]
models/lock/UAL_gear.stl
32.3 x 32.1 x 6.69

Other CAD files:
models/lock/UAL_rack_cover.stl
models/lock/UAL_servo_cover.stl
models/lock/Universal_Arduino_Lock.skp

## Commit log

2020-03-26 chamber block
2020-03-27 electrodes subpage
2020-04-07 3d printable lock model added
    [UAL_all.stl, UAL_all_LT.stl, UAL_baseplate.stl, UAL_baseplate_LT.stl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]
